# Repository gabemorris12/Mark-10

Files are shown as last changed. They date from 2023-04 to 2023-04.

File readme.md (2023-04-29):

# Purpose

The purpose of this project is to receive data from a Mark-10 force transmitter and send the data over to a PC via
bluetooth. A raspberry pi is used to receive data through a serial connection from the Mark 10, then the test begins and
ends when the user presses the start/stop button. Once the button is pressed to stop the test, the pi sends the force
data to a computer, then the computer stores and shows a plot of the data. There are three lights being controlled with
the following usages:

* Blue Light - This indicates that the raspberry pi is connected to the computer. If flashing, then that means that the
  pi is booting up and is not connected to the server through bluetooth.
* Yellow Light - This indicates that the raspberry pi is receiving data from the Mark 10. If flashing, then that means
  that the pi was booted, but the Mark 10 is not plugged up. The Mark 10 can be powered off at boot up, but it must be
  at least plugged up to get past the boot up stage.
* Green Light - This indicates that the test data is being recorded. If flashing, then that means that the button was
  pressed and the above two lights were not on.

# Installation and Set-Up

## Mark 10

The Mark 10 device must be set to units of either lbF, kgF, or kN. The other units will not work with the compressive
load cell. If other units are used, such as with torque load cells, the unit field in the data files/graphs will be left
blank.

### Configuring the Serial Output

Select the Menu button, then select the Serial/USB Settings option. Ensure that the baudrate is set to 9600. If a value
other than 9600 is desired, then add an argument to the serial object in the `rpi_main.py` file
(`data = SerialConnection(SERIAL_PORT, baudrate=19200)`) and make sure that the value matches the setting of the Mark 10.

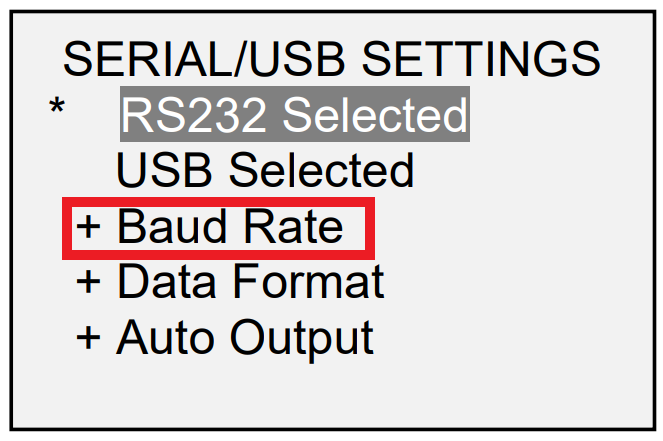
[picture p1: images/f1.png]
image not found


Next, make sure that the Mark 10 is sending data through the USB automatically. Select Auto Output, then the Enabled
button.

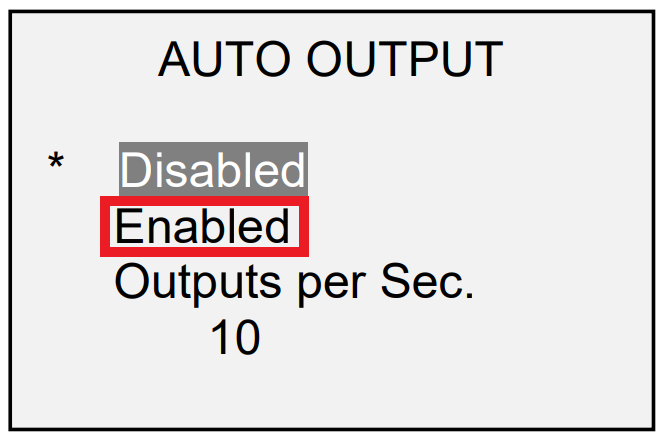
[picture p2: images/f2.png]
image not found


Additionally, the Outputs per Sec. value must match the values seen in at the top of the `server_connectin.py` and
`rpi_main.py` files. Not ensuring this will result in wrong time data.

Press the Data button on the Mark 10 and notice the flashing arrows in the bottom left corner of the main screen. **If
the arrows are not flashing, then the pi will not be able to run a test, and the yellow light will be off.**

## Raspberry Pi

For setting up the OS, [refer to this video](https://youtu.be/1WDagiA8fdU). However, instead of installing the 32-bit
operating system, install the 64-bit operating system shown below.

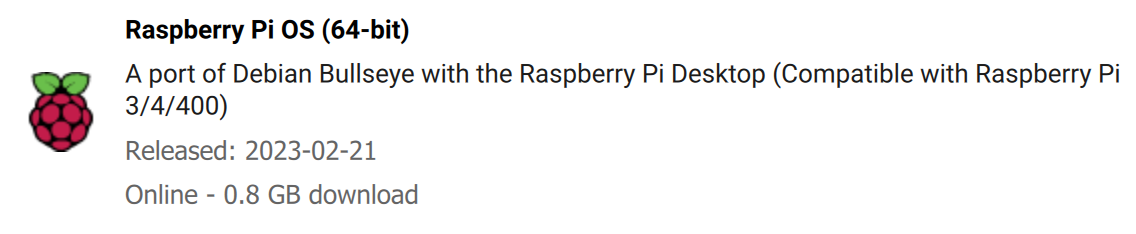
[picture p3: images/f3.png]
image not found


The raspberry pi must be connected to Wi-Fi for this initial set-up in order to download the appropriate packages later
on. If there is a high level of difficulty in getting the past IT as in an industrial setting, then consider connecting
to a personal hot spot.

Make sure that `bluez` is installed by typing in the following in the command prompt,

`sudo apt-get install bluez`

This package is necessary for checking a bluetooth connection at the pi's boot-up.

### Wiring

For wiring the pi, refer to the figure below.

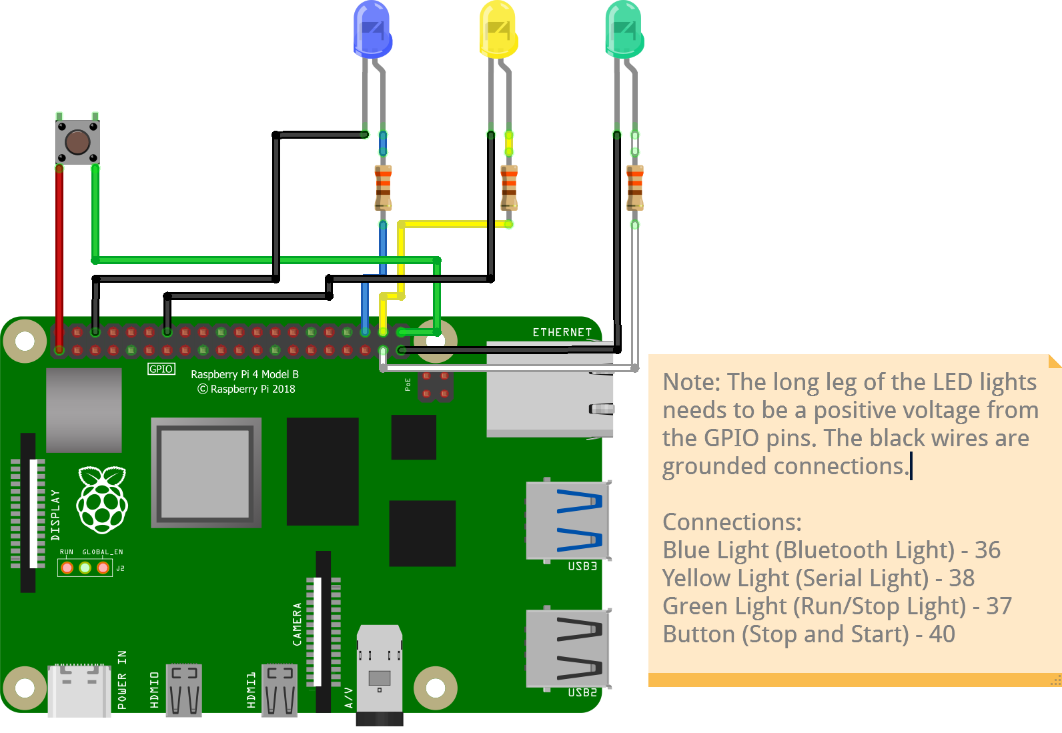
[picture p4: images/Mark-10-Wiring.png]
image not found


The value of the resistors are 330 ohms. The pin numbers shown in the note refer to the board pin numbers as opposed to
the BCM numbering scheme. That is, the board pin numbers refer to the physical layout on the board. Below is a physical
picture for reference.

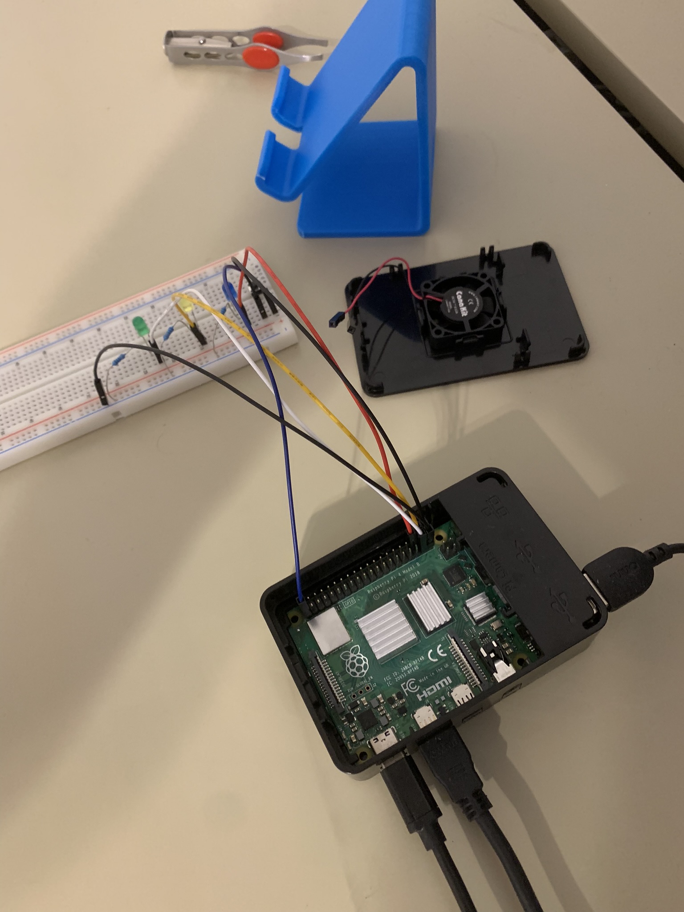
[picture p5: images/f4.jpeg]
image not found


### Setting Up the Python Environment

First, download all the necessary python scripts from this repository. If not familiar with git, then download and
extract the zipfile by navigating to this position:

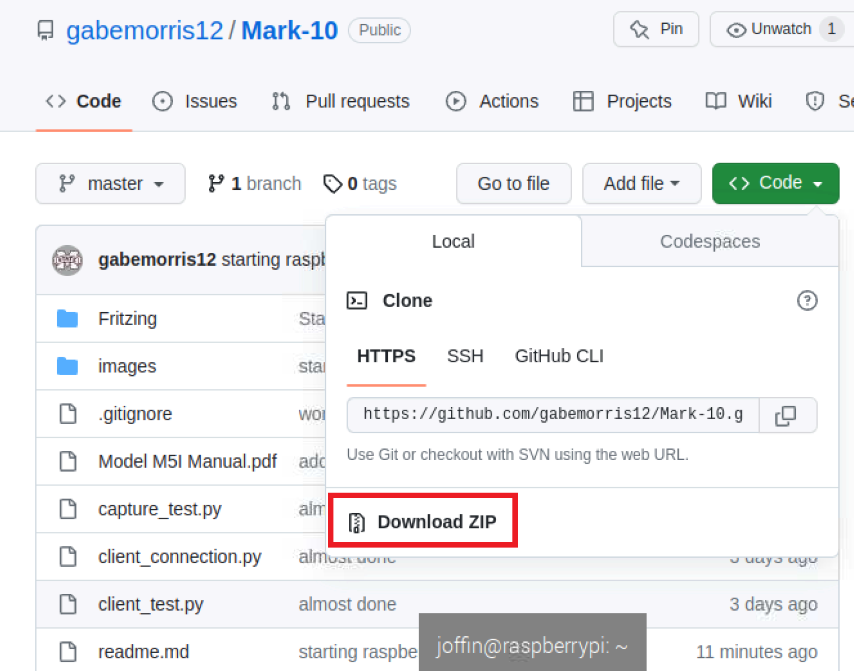
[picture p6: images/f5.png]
image not found


Extracting the zipfile can be done through the pi's file system GUI. Consider placing the project into the desktop.
Next,
run the following commands in the terminal (CTRL+ALT+T) to create a virtual environment.

`cd ~/Desktop/Mark-10-master`

`python3 -m venv venv`

`source venv/bin/activate`

`pip install pyserial RPi.GPIO matplotlib`

Now running `pip list` should output the following,

```angular2html
Package             Version
------------------- -------
contourpy           1.0.7
cycler              0.11.0
fonttools           4.39.3
importlib-resources 5.12.0
kiwisolver          1.4.4
matplotlib          3.7.1
numpy               1.24.3
packaging           23.1
Pillow              9.5.0
pip                 20.3.4
pkg-resources       0.0.0
pyparsing           3.0.9
pyserial            3.5
python-dateutil     2.8.2
RPi.GPIO            0.7.1
setuptools          44.1.1
six                 1.16.0
zipp                3.15.0
```

### Checking the Serial Connection

Making sure the Mark 10 is plugged up, run the following,

`ls /dev | grep tty*`

Toward the bottom of the output, there should be a `ttyUSB0` path. Ensure that this path matches that shown at the top
of the `rpi_main.py` script.

At this point, running the `serial_light_test.py` file should be successful. Make sure that the wiring is completed from
above, and that the virtual environment is activated still (should see "venv" to the left of the current path), and the
Mark 10 is plugged up, then run `python serial_light_test.py` from the terminal. The script will run for about 11
seconds, and pressing the Data button on the Mark 10 should toggle the yellow light on and off.

### Configuring the Pi to Run at Boot-Up

In order to run the software in a state where the raspberry pi is not tethered to a screen or keyboard, the script needs
to be executed at the boot-up of the device. This is done by first modifying the `rpi_bash.sh` script. The script path
in that file needs to be modified. First, run the following,

`nano rpi_bash.sh`

Use the arrow keys to move the cursor and modify the path next to the `cd` command to match the working directory of
the project (`/home/<user name>/Desktop/Mark-10-project`). Note that the path should be in quotes if there are spaces
in the path string. Once finished, press CTRL+X, then "y", then enter. Then run,

`chmod +x rpi_bash.sh` This makes the script executable.

Now to make the script run at boot-up, the `rc.local` file must be modified. Do this by running the following,

`sudo nano /etc/rc.local`

Move the cursor with the arrow keys to a line that is above `exit 0` and below `fi`. Add in

`/bin/bash /home/<user name>/Desktop/Mark-10-master/rpi_bash.sh &`

Press CTRL+X, then "y", then enter. Now running `sudo /etc/rc.local` will run the `rpi_main.py` script, and a blinking
blue light should be observed. If that script executes, then the script will run at boot up. If the blue light begins
flashing, then that means that the pi is not connected to the server through bluetooth. To end the script, the process 
for the `rpi_bash` sequence must be found and terminated. The script is being run in the background, but this can be 
done by running the following,

`ps aux | grep rpi_bash`

Find the process's PID number in the second column, then run

`sudo kill <PID number>`

Additionally, if ever troubleshooting in the future, it is important that the `rpi_main.py` script be ended before
attempting to run it manually. Find the PID sequence by running `ps aux | grep rpi_main` and eliminate it as above.

### Bluetooth Pairing

The raspberry pi needs to be paired to the server computer before being able to run the script. Turn on bluetooth on
both the raspberry pi and the Windows computer. Next, click on Add Device from the raspberry pi's bluetooth settings:

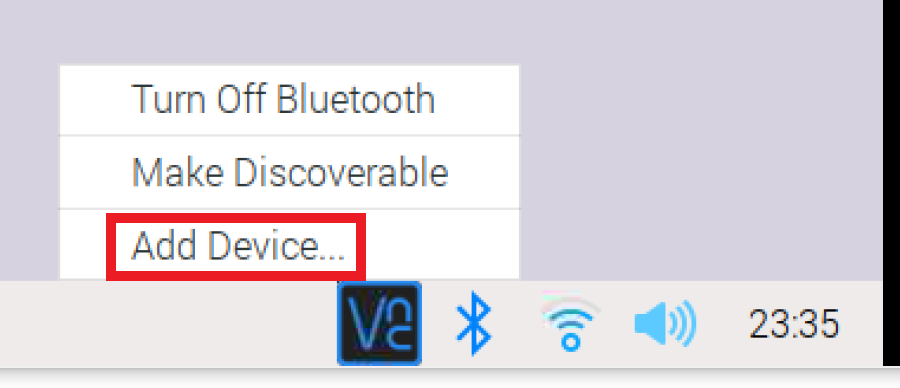
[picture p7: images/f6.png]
image not found


Select the desired device, then click pair:

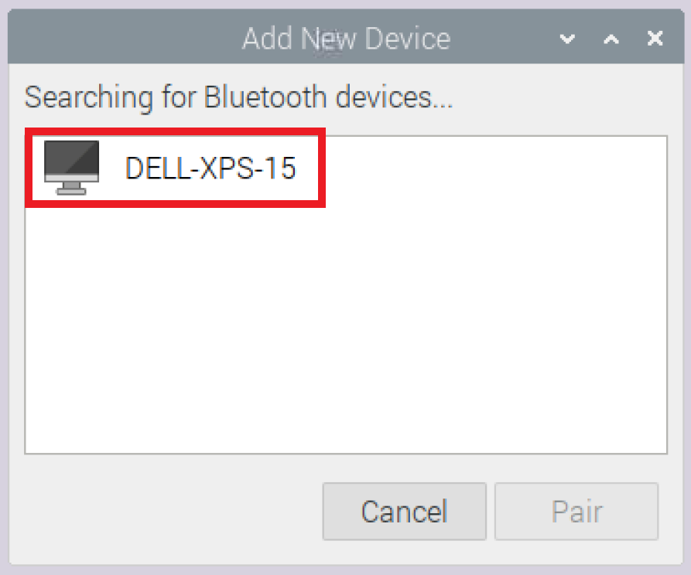
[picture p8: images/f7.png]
image not found


Once initiated, both the raspberry pi and the computer will receive a pop-up like this:

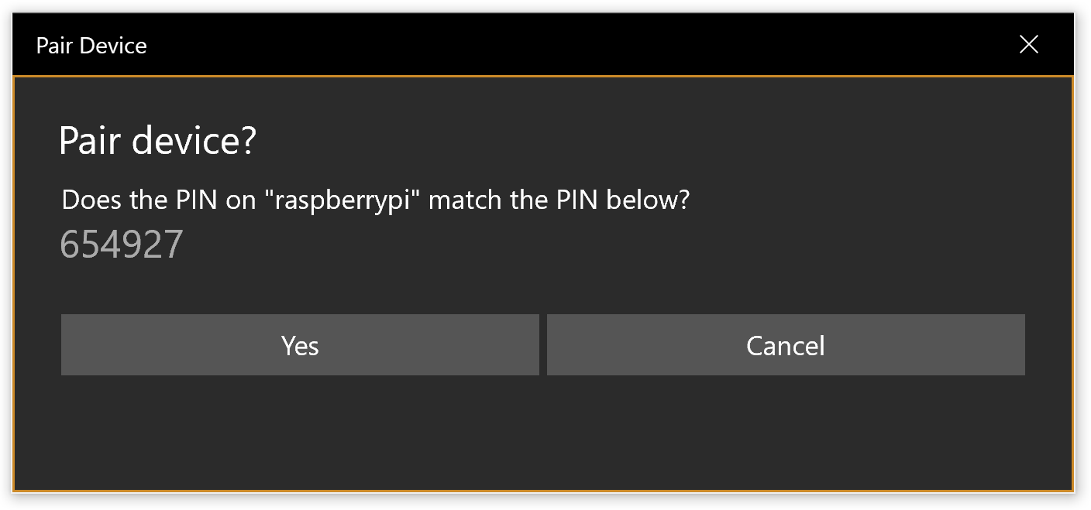
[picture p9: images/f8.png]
image not found


Click Yes on both of them quickly before the response times out. Next, navigate to the Devices and printers screen:

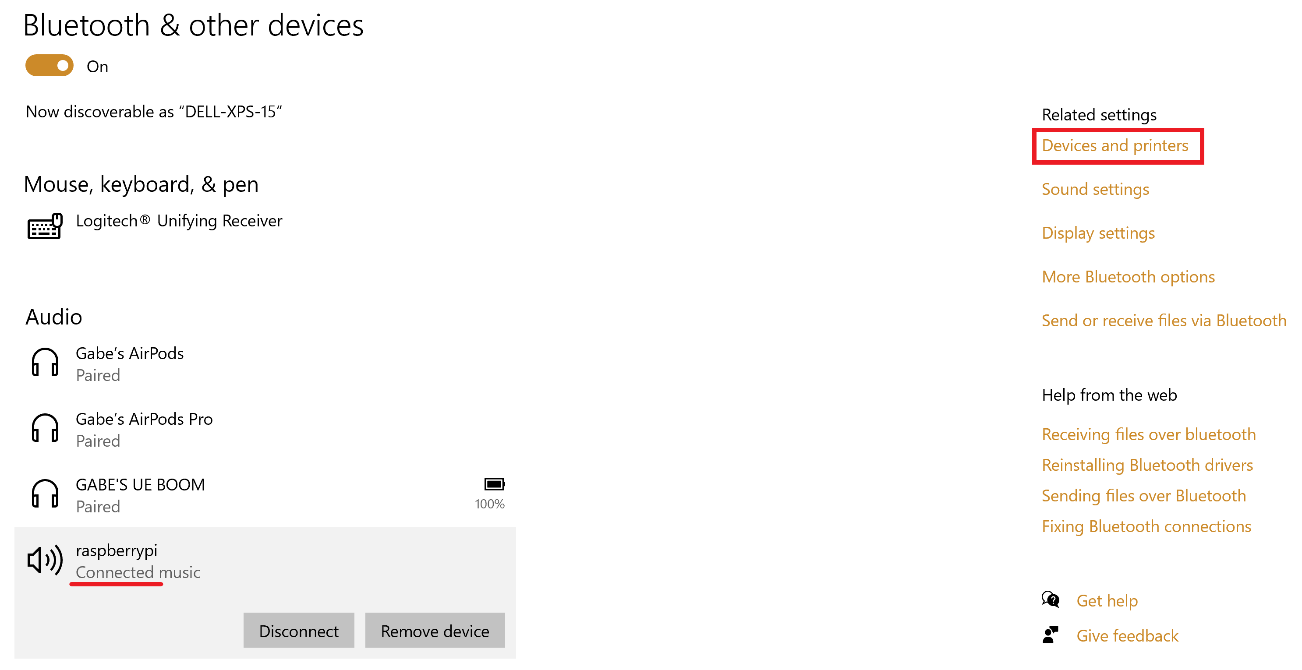
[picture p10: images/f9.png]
image not found


Note, a paired device does not mean that the computer is connected. The computer must be in the connected state in order
to successfully execute the scripts. Next, right-click on raspberrypi, then go to the Bluetooth tab and rename the pi to
the desired name.

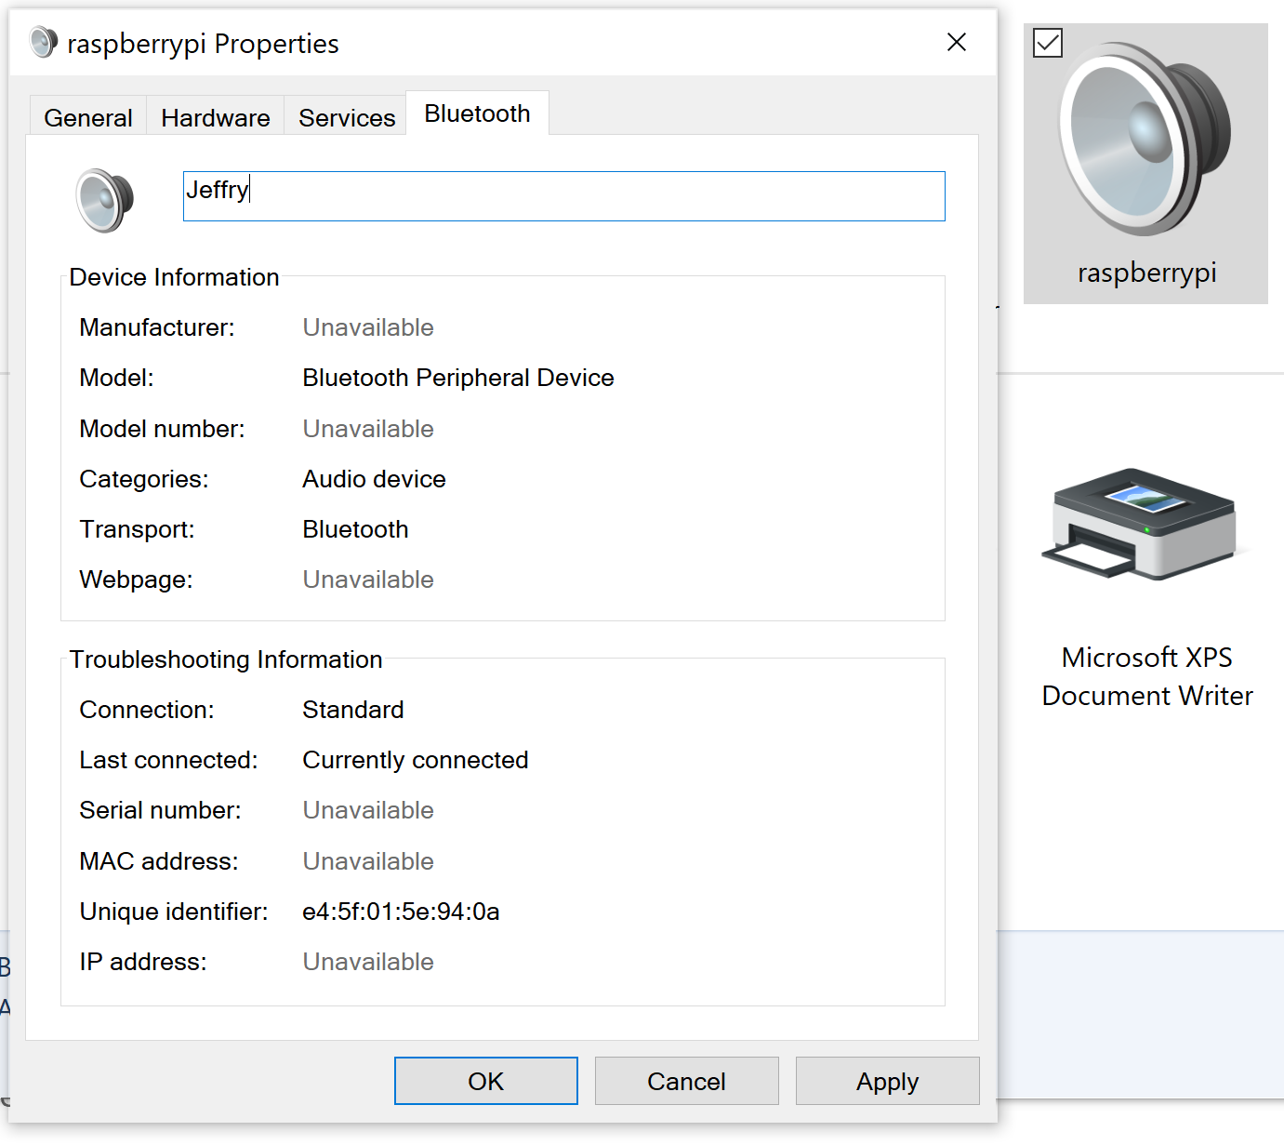
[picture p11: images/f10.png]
image not found


It may be necessary to restart bluetooth on the computer for the name to update. Ensure that the name here matches the
name at the top of the `rpi_main.py` file.

### Finding the Server's MAC Address

On the computer, open up the command prompt. Making sure bluetooth is turned on, run the following command,

`ipconfig /all`

The computer's MAC address is the physical address under the bluetooth network heading. On the raspberry pi, making sure
that the terminal is still in the working directory, run

`nano rpi_main.py`

Use the arrow keys to move to the `ADDRESS` variable declaration, and change the value of the MAC address to match that
seen from above. Press CTRL+X, then "y", then enter.

## Computer

The computer must have python properly installed. Do this by navigating to
the [python downloads page](https://www.python.org/downloads/). Download the latest installer and run it. In an
industrial setting, IT may have to be involved in order to whitelist running python or the installer. Select custom
installation.

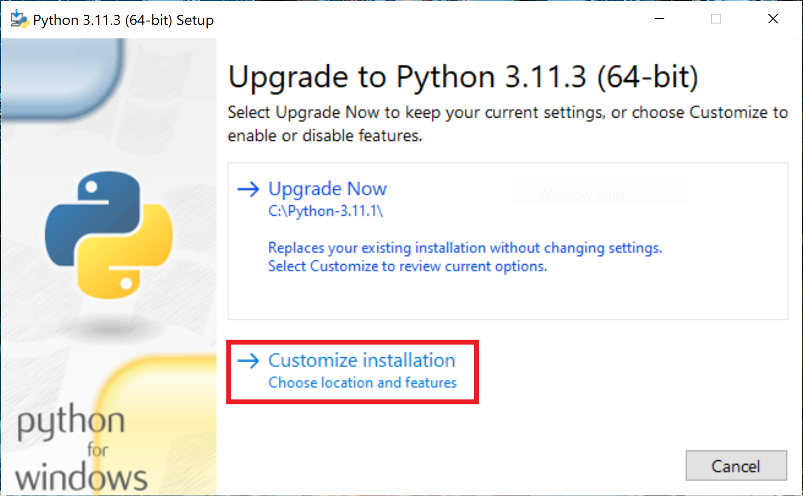
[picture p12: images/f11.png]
image not found


Leave the default optional features checked. Click next. Ensure that the Add Python to environment variables is
selected, and install python in the desired directory. It is recommended that python be stored at the root directory as
shown below.

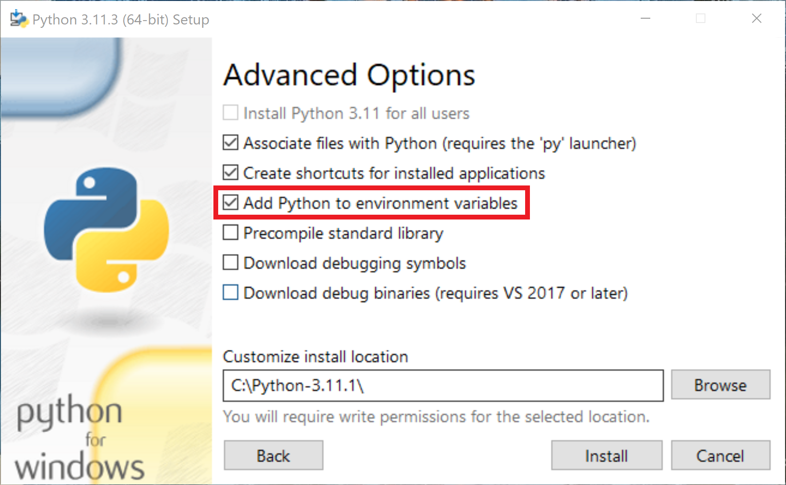
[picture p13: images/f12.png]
image not found


Click install. Now the installer can be deleted, and running `python --version` in the command prompt should output the
version just installed (assuming there are no other installations of python interfering). If the windows store launches,
then that means that python was not added to the environment variables.

### Setting up the Python Environment

Download the necessary files as done in the raspberry pi set-up. Consider placing the Mark-10-master folder in the 
desktop and navigate to this working directory's position in the command prompt using `cd`. Run the following,

`python -m venv venv`

`venv\Scripts\activate`

`pip install matplotlib`

Open the `server_connection.py` file in Notepad and modify the `ADDRESS` variable to match the address from above. Now
running `python server_connection.py` in the command prompt will launch the server, and it will begin listening for the
raspberry pi. Bluetooth has to be turned on in order for the server to start running.

Next, boot up the raspberry pi. If the blue light starts flashing then that means that the computer did not make the 
connection automatically. Open the bluetooth settings on the computer and connect to the pi. If the Mark 10 is also 
plugged up, the yellow light and the blue light should turn solid, and there should be a message in the server script
indicating a connection. Now pressing the button should begin recording the data and the green light should come on. 
There should be message saying that units have been received. Press the button again to end the test. A plot should 
automatically pop up.

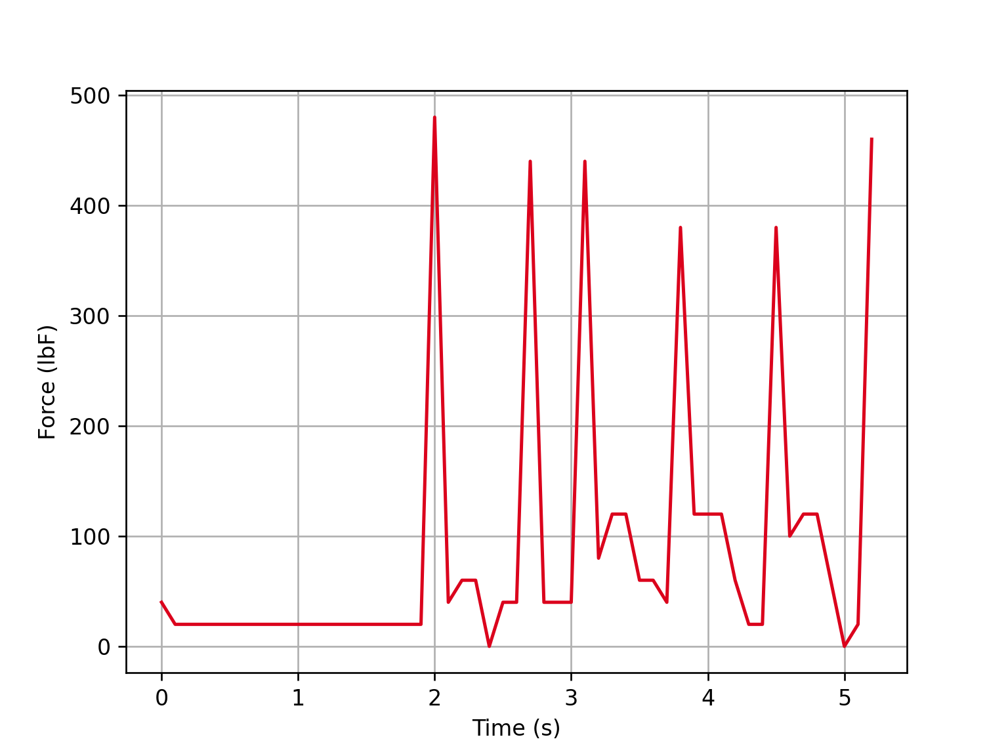
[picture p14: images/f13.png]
image not found


The data gets stored in the working directory to a folder called `data` both locally to the raspberry pi and on the 
computer. To make it easier to run the server, modify the path in the `server.bat` file by right-clicking on it in the 
file manager and pressing edit. Now the file can be moved to the desktop and double-clicking on it will run the server.
Running the batch file, however, may alert anti-malware software. Be sure to whitelist this process, or consult IT if
in an industrial setting.

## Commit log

2023-04-25 Starting the readme
    [Mark 10 Wiring.fzz]
2023-04-26 starting raspberry pi installation
2023-04-29 fixed error_flash pin number
2023-04-29 fixed pin number for error_flash function
2023-04-29 Finshed raspberry pi documentation
